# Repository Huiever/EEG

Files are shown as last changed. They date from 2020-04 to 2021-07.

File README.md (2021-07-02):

# 脑电放大器说明文档

version：V1.0.0         author：lyh

## 准备

- windows系统电脑一台

- 下载并安装[CH340驱动](http://www.wch.cn/downloads/file/65.html?time=2020-10-26%2015:34:02&code=aVN9CyCuR4TqbKSTNDEmppEj6408df6NMeNtbwHk)

- 下载[Openbci_GUI V4.2.0](https://github.com/OpenBCI/OpenBCI_GUI/releases/tag/v4.2.0)，更高版本目前还无法支持

- 放大器硬件接口说明

  1. **SWD程序下载接口**：烧录固件使用
  2. **电源接口**：电源输出，测试使用.`AVDD`,`AVSS`分别为`ads1299`正负输入电源，为`+-2.5V`
  3. **电极接口**：`INxP`,`INxN`(x=1,2,...,8)分别为8个通道的正负输入，`REF`为参考电极输入，`BIAS`为右腿驱动输入
  4. **电源开关**：按下为OFF，**弹起**为**ON**
  5. **`HC05`蓝牙接口**：若使用`HC05`蓝牙，将7中跳线帽选择`HC05`，同时蓝牙模块插入时应注意方向，模块朝板内，也可根据模块上的丝印匹配来插入
  6. **电池接口(背面)**：3.7V锂电池输入，**请勿反接或短路**
  7. **蓝牙选择**：利用跳线帽选择蓝牙为`nRF52832`or`HC05`
  8. **通信线路跳线帽**：连接`ads1299`和`stm32f407`,取下跳线帽则对应通信断开
  9. **充电指示灯**：充电时亮红灯，充满亮绿灯
  10. **LED显示**：放大器上丝印有误，从上往下分别为`PWR`,`LED1`,`LED0`，**电源ON**时`PWR`点亮
  11. **`MicroUSB`接口**：供电以及对电池充电，还可作为有线串口使用
  12. **按键**：`RESET`控制程序复位，`KEY1`,`KEY2`为自定义按键，编程使用

  

## 开始

1. 打开`Openbci_GUI`，将microUSB线一端插入电脑，另一端接入放大器

2. 对脑电电极涂上导电膏，固定在头部，另一端根据需要接在放大器的指定位置.采用单极导联的时候，参考电极接`REF`，其余电极接`INxP`.双极导联的时候`INxP`,`INxN`交替连接.程序默认为单极导联模式

3. 打开放大器的电源开关

4. 在`Openbci_GUI`界面，依次点选`LIVE(from Cyton)`,`Serial(from Dongle)`，最后点击`AUTO_CONNECT`等待数秒钟即可启动放大器并进入波形显示界面

   
   


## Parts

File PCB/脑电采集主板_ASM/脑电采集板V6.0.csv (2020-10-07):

Comment | Description | Designator | Footprint | LibRef | Pins | Quantity
100nF | 贴片电容 | C1, C3, C6, C7, C8, C11, C12, C28, C46, C47, C48, C49, C50, C51, C52, C53, C54, C55, C56, C57, C89, C93 | 0402_C | 0402 100nF (104) 10% 16V | 2 | 22
10uF | 贴片电容 | C2, C9, C10, C13, C15, C17, C18, C20, C23, C24, C32, C33, C88 | 0402_C | 0402 10uF (106) 20% 6.3V | 2 | 13
10uF (106) 20% 6.3V | 贴片电容 | C4 | 0402_C | 0402 10uF (106) 20% 6.3V | 2 | 1
100nF (104) 10% 16V | 贴片电容 | C5 | 0402_C | 0402 100nF (104) 10% 16V | 2 | 1
1uF | 贴片电容 | C14, C16, C19, C21, C25, C26, C27 | 0402_C | 0603 1uF (105) 10% 50V | 2 | 7
2.2uF | 贴片电容 | C22, C30, C31 | 0603_C | 0603 2.2uF (225) 10% 16V | 2 | 3
10nF | 贴片电容 | C29, C34, C75 | 0402_C | 0402 10nF (103) 10% 50V | 2 | 3
10pF | 贴片电容 | C35, C36 | 0402_C | 0603 10pF (100) 5% 50V | 2 | 2
22pF | 贴片电容 | C37, C38, C90, C96 | 0402_C | 0603 22pF (220) 5% 50V, 0402 22pF (220) 5% 50V | 2 | 4
10uF 10V | 贴片电容 | C39, C43 | 0402_C | 0603 10uF (106) 10% 10V | 2 | 2
100nF 50V | 贴片电容 | C40, C41, C44 | 0402_C | 0603 100nF (104) 10% 50V | 2 | 3
2.2uF 16V | 贴片电容 | C42 | 0603_C | 0603 2.2uF (225) 10% 16V | 2 | 1
2.2uF (225) 10% 16V | 贴片电容 | C45 | 0603_C | 0603 2.2uF (225) 10% 16V | 2 | 1
4.7nF | 贴片电容 | C58, C59, C60, C61, C62, C63, C64, C65, C66, C67, C68, C69, C70, C71, C72, C73, C74 | 0603_C | 0402 4.7nF (472) 10% 50V | 2 | 17
1uF 50V | 贴片电容 | C76, C78, C80, C82, C84, C86 | 0402_C | 0603 10nF (103) 10% 50V | 2 | 6
100nF 50V | 贴片电容 | C77, C79, C81, C83, C85, C87 | 0402_C | 0603 10nF (103) 10% 50V | 2 | 6
100uF | 钽电容 | C91 | CASE-B_3528 | 3528 100uF (107) 10% 6.3V | 2 | 1
1uF | 贴片电容 | C92, C94, C95 | 0603_C | 0603 1uF (105) 10% 50V | 2 | 3
SS210 | 二极管 | D1 | SMA(DO-214AC)_S1 | SMA(DO-214AC) SS210 | 2 | 1
红灯 0603 | 发光二极管 | D2, LED0 | 0603_LED_S1 | 0603 红灯 | 2 | 2
绿灯 0603 | 发光二极管 | D3, LED1, PWR | 0603_LED_S1 | 0603 绿灯 | 2 | 3
Fuse 1A | Fuse | F1 | 0805_R | Fuse 2 | 2 | 1
SW-PB | Switch | KEY1, KEY2, RESET | KEY_3.6*2.5 | SW-PB | 2 | 3
3.3uH±10% | 贴片电感 | L1, L2, L3, L4 | 0805_L | 0805 3.3uH10% | 2 | 4
蓝牙选择 | Header, 3-Pin, Dual row | P1 | HDR2X3 | Header 3X2 | 6 | 1
HC-05_CON | Header, 6-Pin | P2 | HDR1X6 | Header 6 | 6 | 1
USB | Header, 5-Pin | P3 | MICRO-USB | Header 5 | 7 | 1
电源 | Header, 5-Pin, Dual row | P5 | HDR2X5 | Header 5X2 | 10 | 1
battery | Header, 2-Pin | P6 | HDR1X2 | Header 2 | 2 | 1
SWD | Header, 4-Pin | P7 | HDR1X4 | Header 4 | 4 | 1
Header 9X2 | Header, 9-Pin, Dual row | P8 | HDR2X9 | Header 9X2 | 18 | 1
Header 8X2 | Header, 8-Pin, Dual row | P9 | HDR2X8 | Header 8X2 | 16 | 1
BSS84LT1G | MOS(场效应管) | Q1 | SOT-23(SOT-23-3) | BSS84LT1G | 3 | 1
47KΩ | 贴片电阻 | R1, R2, R3, R5, R6 | 0402_R | 0402 47KΩ (4702) 1% | 2 | 5
4.7KΩ | 贴片电阻 | R7, R9 | 0402_R | 0402 4.7KΩ (4701) 1% | 2 | 2
120Ω | 贴片电阻 | R8, R10, R12, R13 | 0402_R | 0402 120Ω (1200) 1% | 2 | 4
10KΩ | 贴片电阻 | R11 | 0402_R | 0402 10KΩ (1002) 1% | 2 | 1
100KΩ | 贴片电阻 | R14, R15 | 0402_R | 0402 100KΩ (1003) 1% | 2 | 2
1.2KΩ | 贴片电阻 | R16 | 0402_R | 0402 1.2KΩ (1201) 1% | 2 | 1
1KΩ | 贴片电阻 | R17, R21 | 0402_R | 0402 1KΩ (1001) 1%, 0603 1KΩ (1001) 1% | 2 | 2
0Ω | 贴片电阻 | R18 | 0402_R | 0603 0Ω (0R0) 1% | 2 | 1
510Ω | 贴片电阻 | R19, R20 | 0402_R | 0603 510Ω (5100) 1% | 2 | 2
1MΩ | 贴片电阻 | R22 | 0402_R | 0603 1.2MΩ (1204) 1% | 2 | 1
10K | 贴片电阻 | R23, R26, R27, R28, R29 | 0402_R | 0603 10Ω (10R0) 1% | 2 | 5
10Ω | 贴片电阻 | R24 | 0402_R | 0603 10Ω (10R0) 1% | 2 | 1
10Ω (10R0) ±1% | 贴片电阻 | R25 | 0402_R | 0603 10Ω (10R0) 1% | 2 | 1
4.99KΩ | 贴片电阻 | R30, R31, R32, R33, R34, R35, R36, R37, R38, R39, R40, R41, R42, R43, R44, R45, R46 | 0603_R | 0603 4.99KΩ (4991) 1% | 2 | 17
390KΩ | 贴片电阻 | R47 | 0603_R | 0603 390KΩ (3903) 1% | 2 | 1
2KΩ | 贴片电阻 | R48 | 0402_R | 0402 2KΩ (2001) 1% | 2 | 1
0Ω (0R0) ±1% | 贴片电阻 | R49 | 0402_R | 0402 0Ω (0R0) 1% | 2 | 1
SW-PB | Switch | S1 | KEY_5.8*5.8 | SW-PB | 6 | 1
nRF52832 |  | U1 | nRF52832 | nRF52832 | 24 | 1
TF_Card |  | U2 | TF_1 | TF_Card | 14 | 1
CH340G | USB | U3 | SOIC-16_150mil | CH340G_[C14267] | 16 | 1
MPU-6050 | 传感器 | U4 | QFN-24_4x4x05P | MPU-6050_[C24112] | 25 | 1
TP4056 | 电池电源管理 | U5 | SOP-8_EP_150mil | TP4056_[C16581] | 9 | 1
TPS60403 |  | U6 | SOT-23-5 | TPS60403 | 5 | 1
TPS73225 |  | U7 | SOT-23-5 | TPS73225 | 5 | 1
TPS71733DCKR |  | U8 | SC-70-5 | TPS71733DCKR | 5 | 1
TPS72325 |  | U9 | SOT-23-5 | TPS72325 | 5 | 1
STM32F429ZGT6 | ARM | U10 | LQFP-144_20x20x05P | STM32F429ZGT6 | 144 | 1
ADS1299IPAG |  | U11 | ADS1299 | ADS1299IPAG | 64 | 1
32.768KHz | 贴片晶振 | Y1 | SMD-3215_2P FC - 135 | SMD-3215_2P 32.768KHz 20ppm 12.5pF | 2 | 1
8MHz | 贴片晶振 | Y2 | SMD-5032_2P | SMD-5032_2P 8MHz 20ppm 20pF | 2 | 1
12MHZ | 贴片晶振 | Y3 | SMD-3225_4P | SMD-3225_4P 12MHZ 20PF 10PPM | 4 | 1

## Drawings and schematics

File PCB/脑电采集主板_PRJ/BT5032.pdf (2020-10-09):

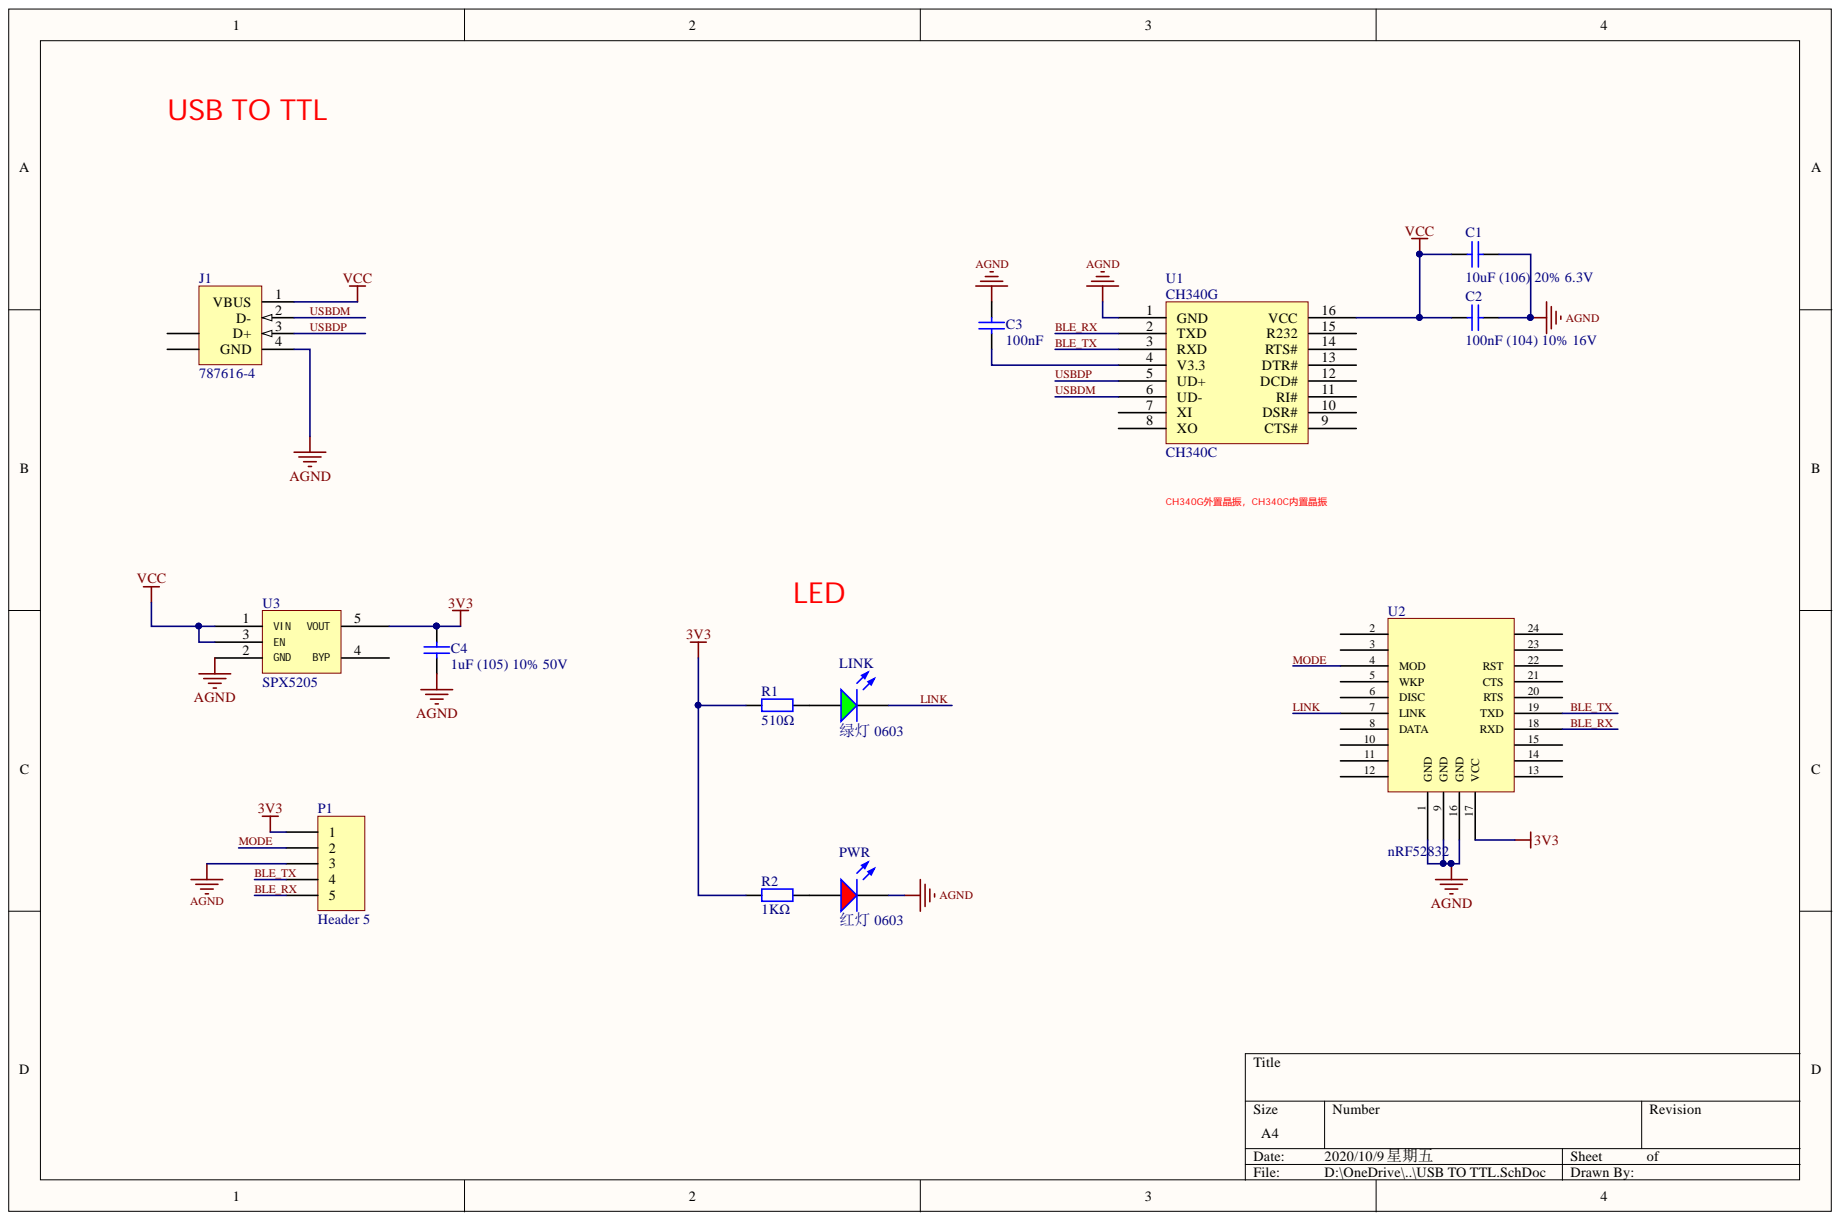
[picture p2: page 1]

VCC 17 RXD 18 TXD 19 RTS 20 CTS 21 RST 22

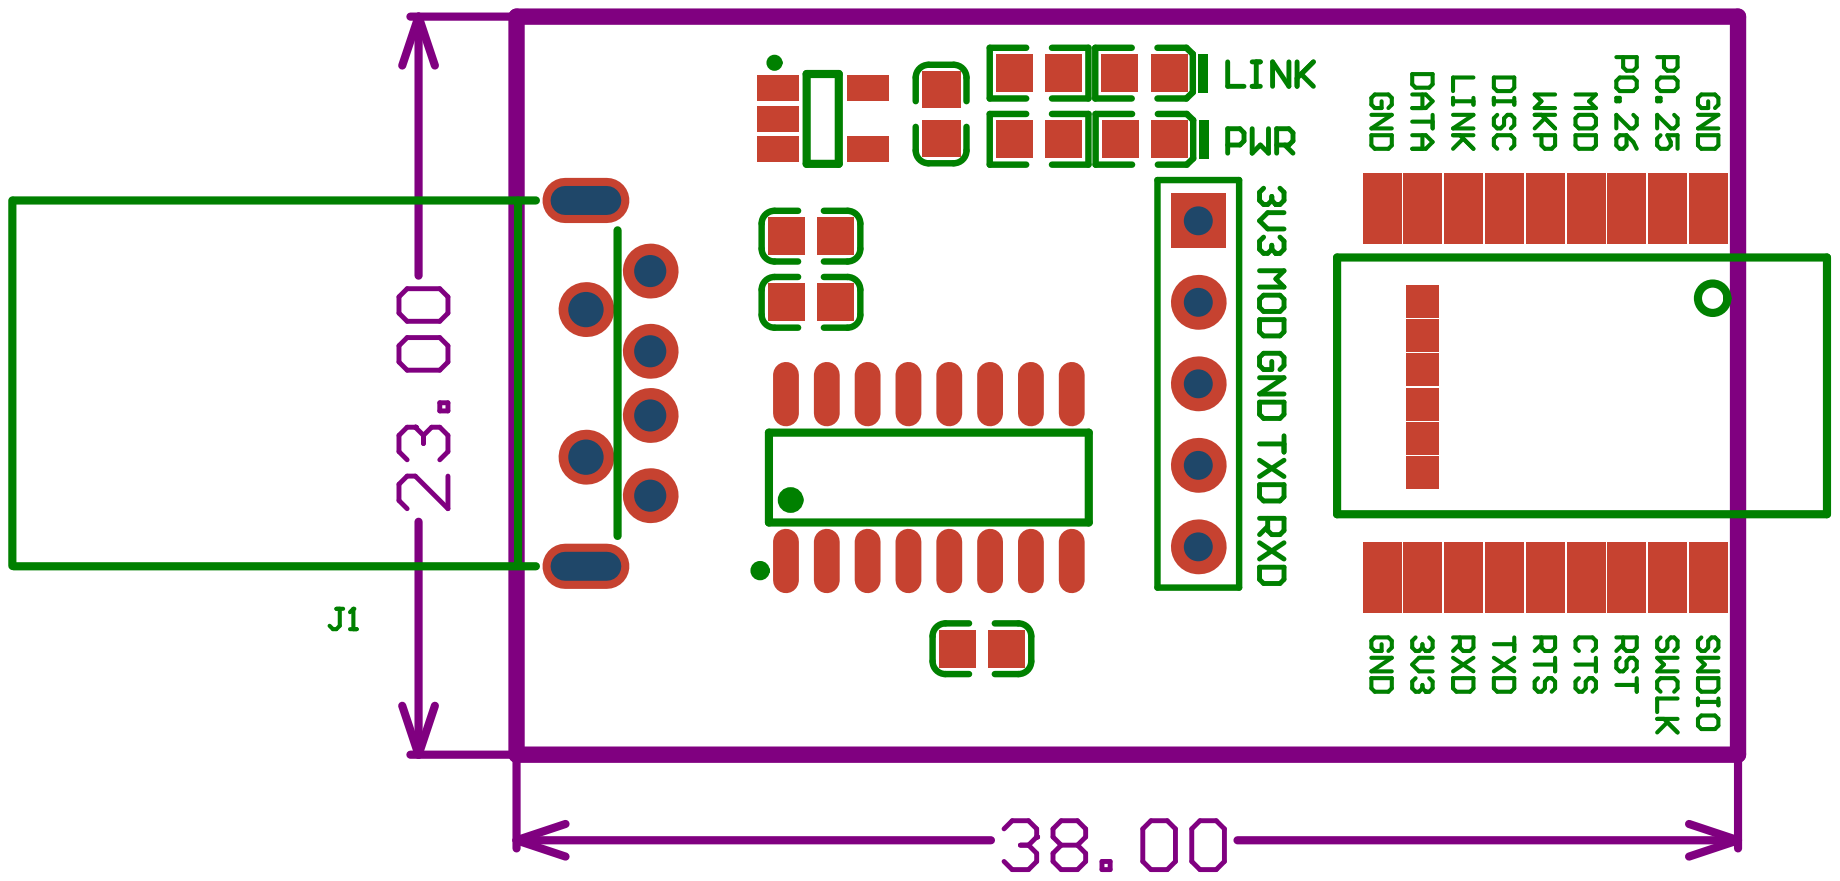
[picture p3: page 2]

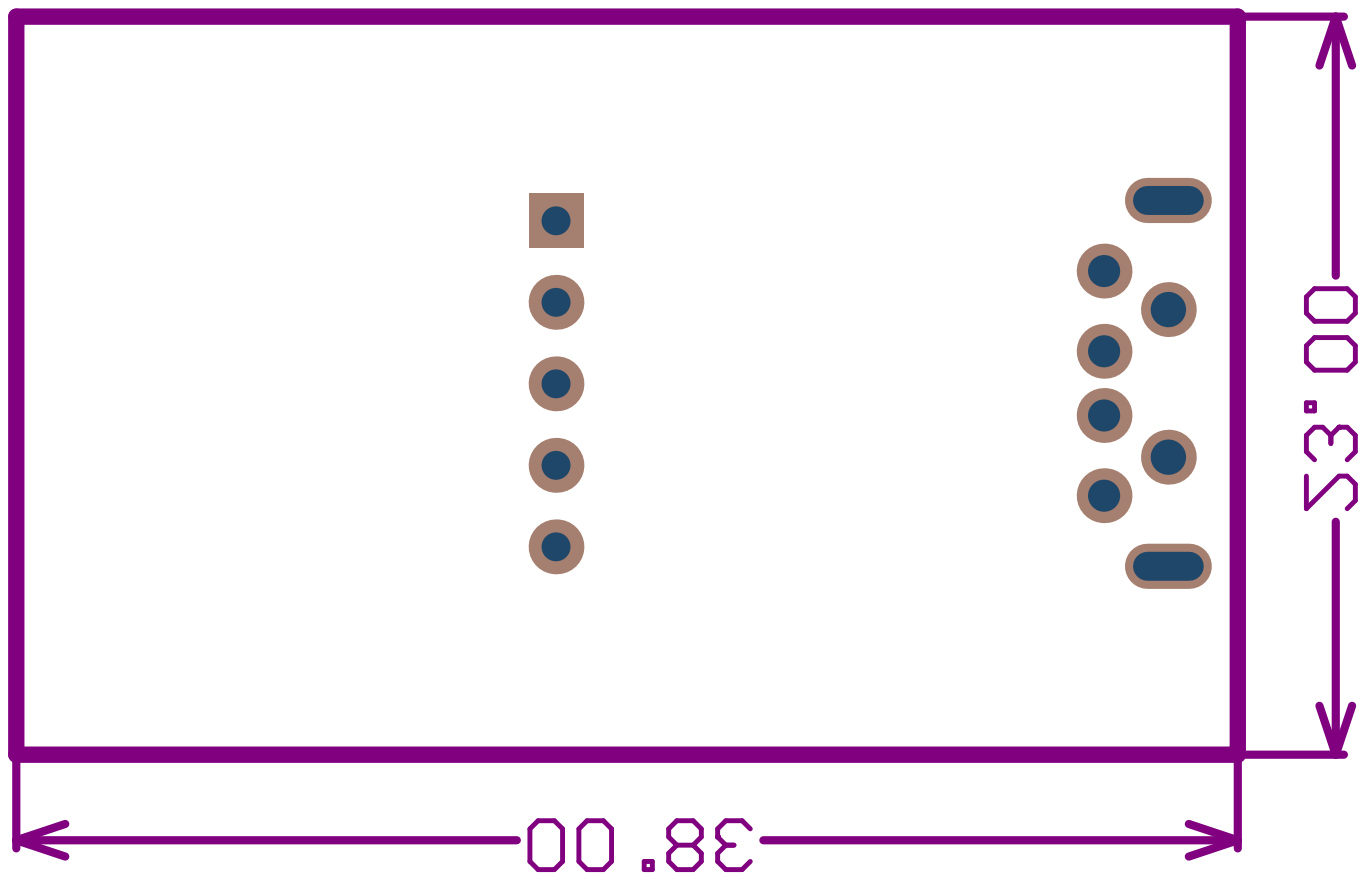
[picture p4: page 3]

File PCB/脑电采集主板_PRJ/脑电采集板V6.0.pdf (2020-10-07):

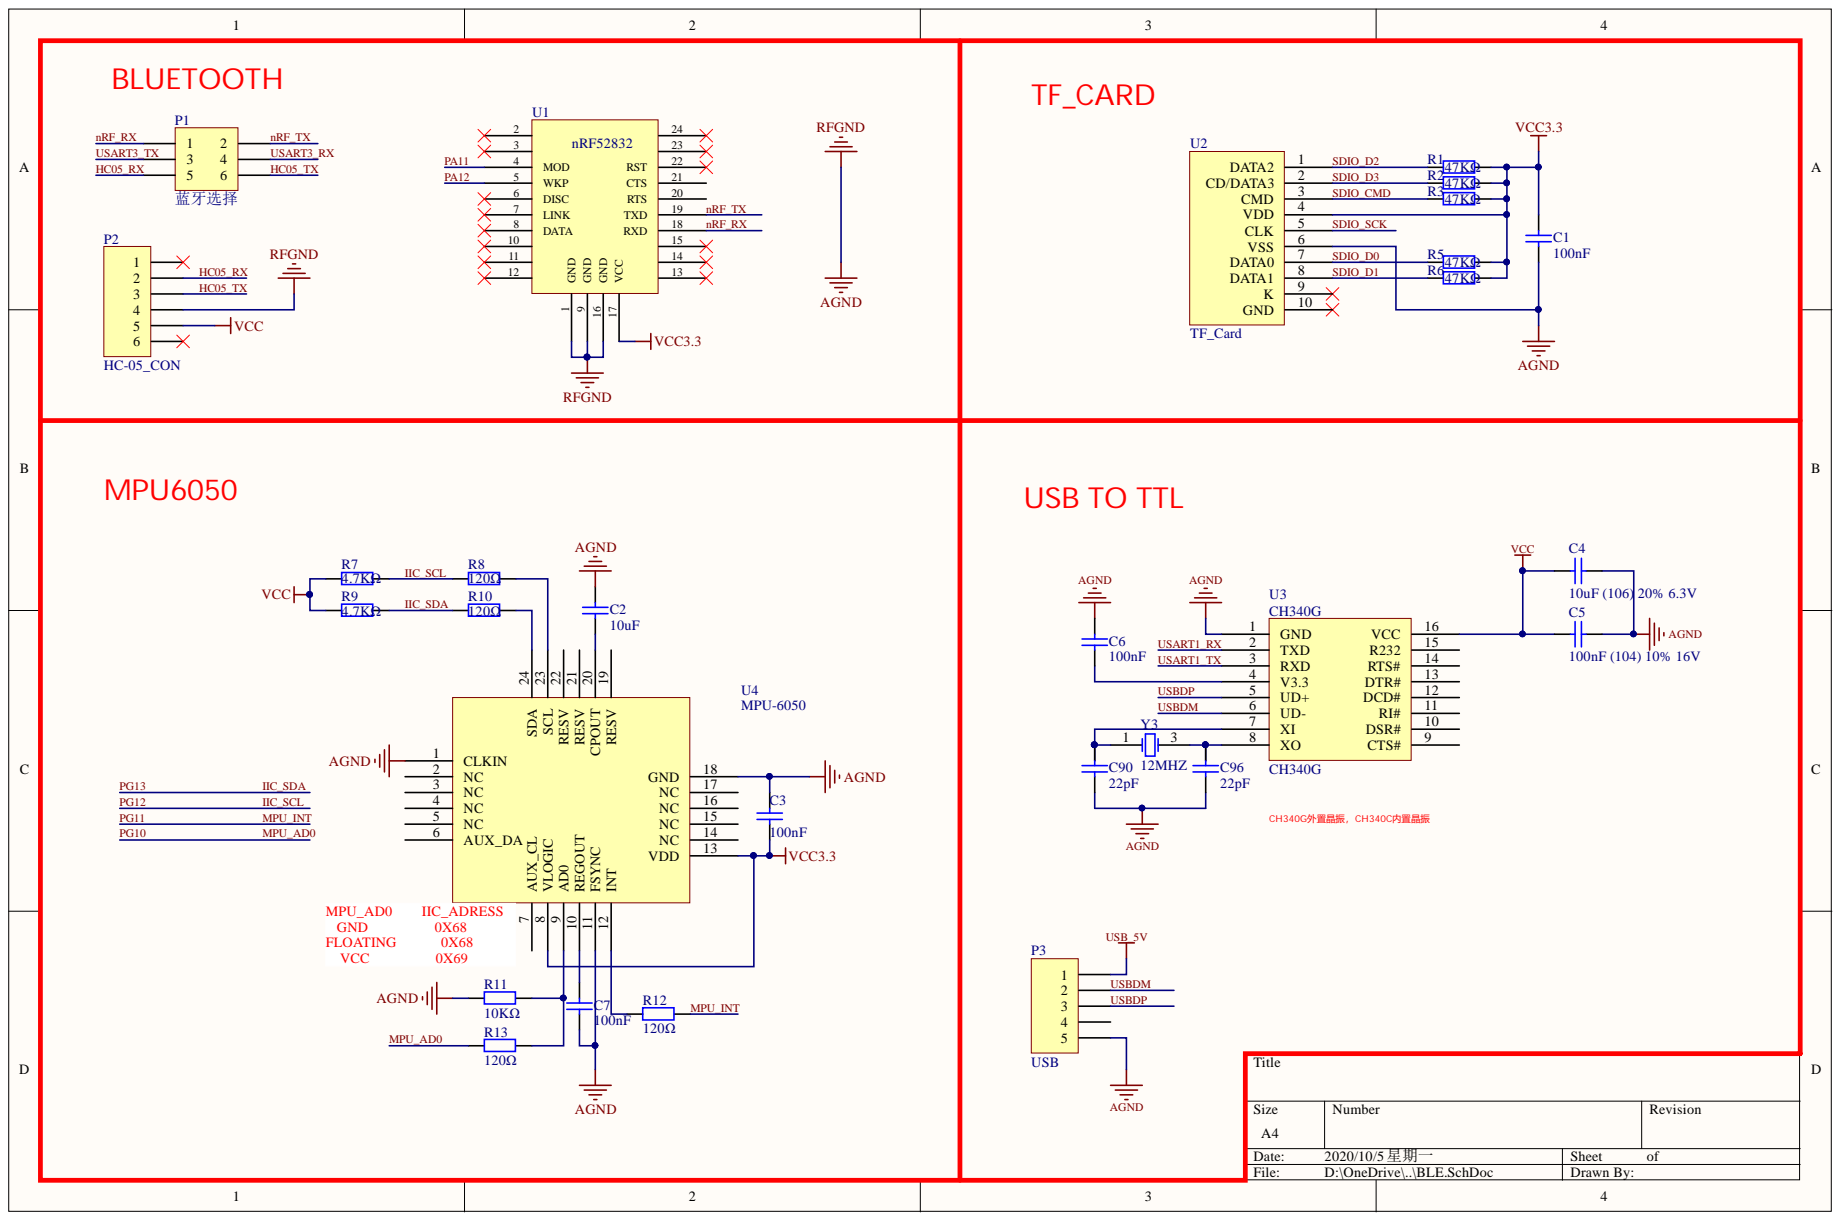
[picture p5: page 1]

VCC 17 RXD 18 TXD 19 RTS 20 CTS 21 RST 22

RESV 19 CPOUT 20 RESV 21 RESV 22 SCL 23 SDA 24

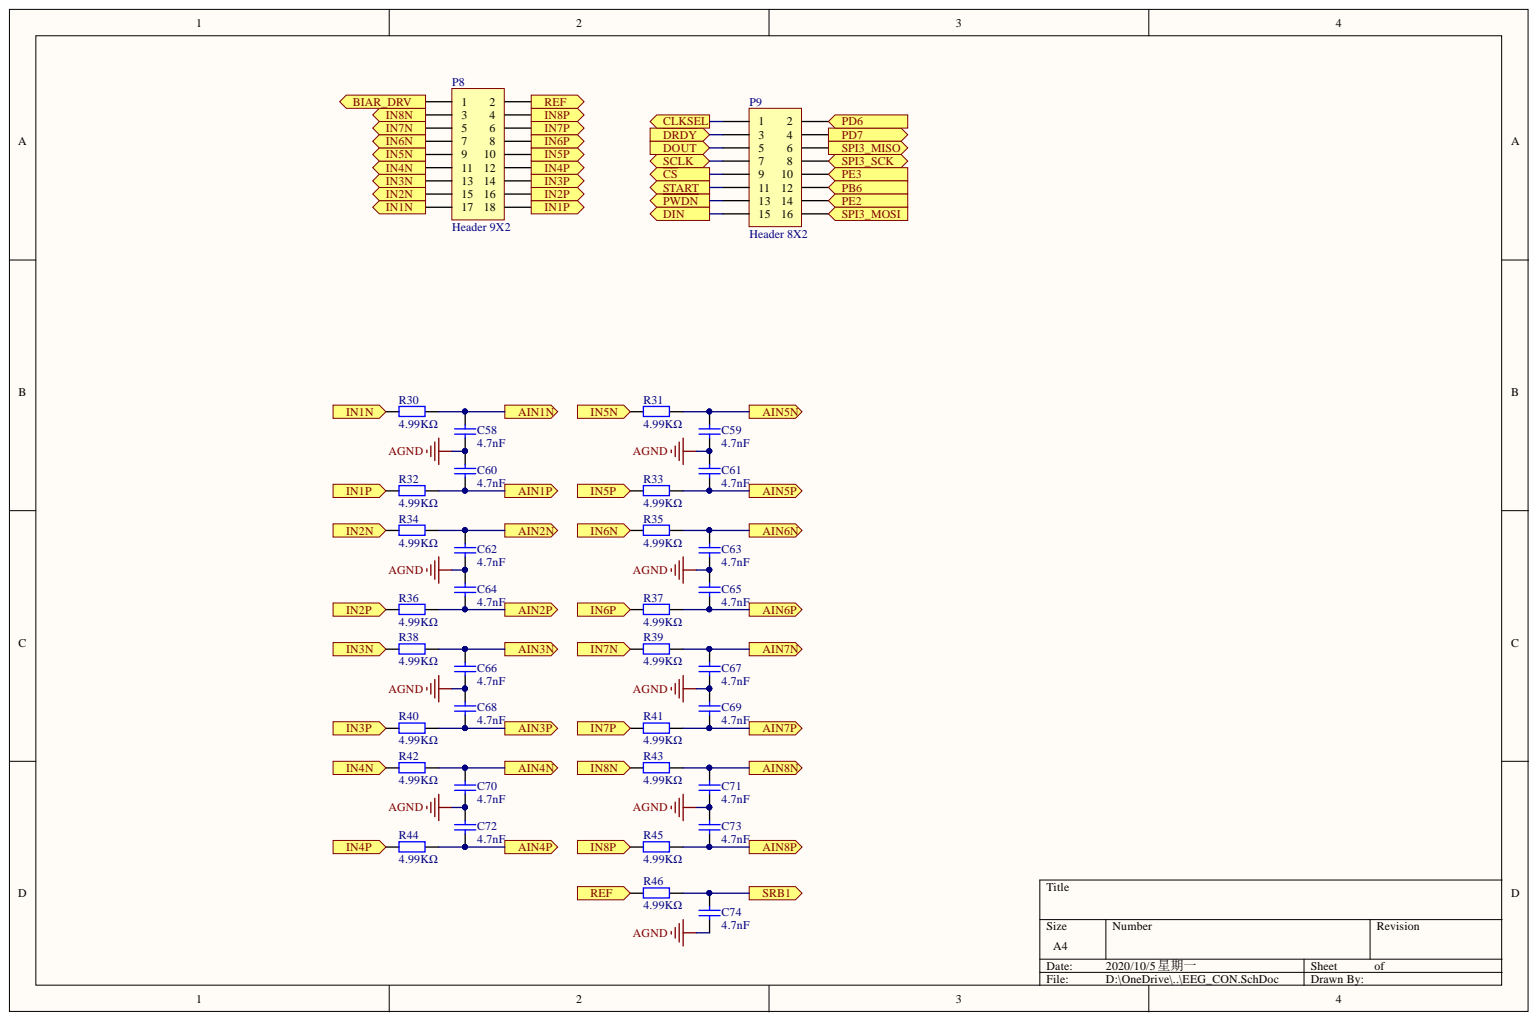
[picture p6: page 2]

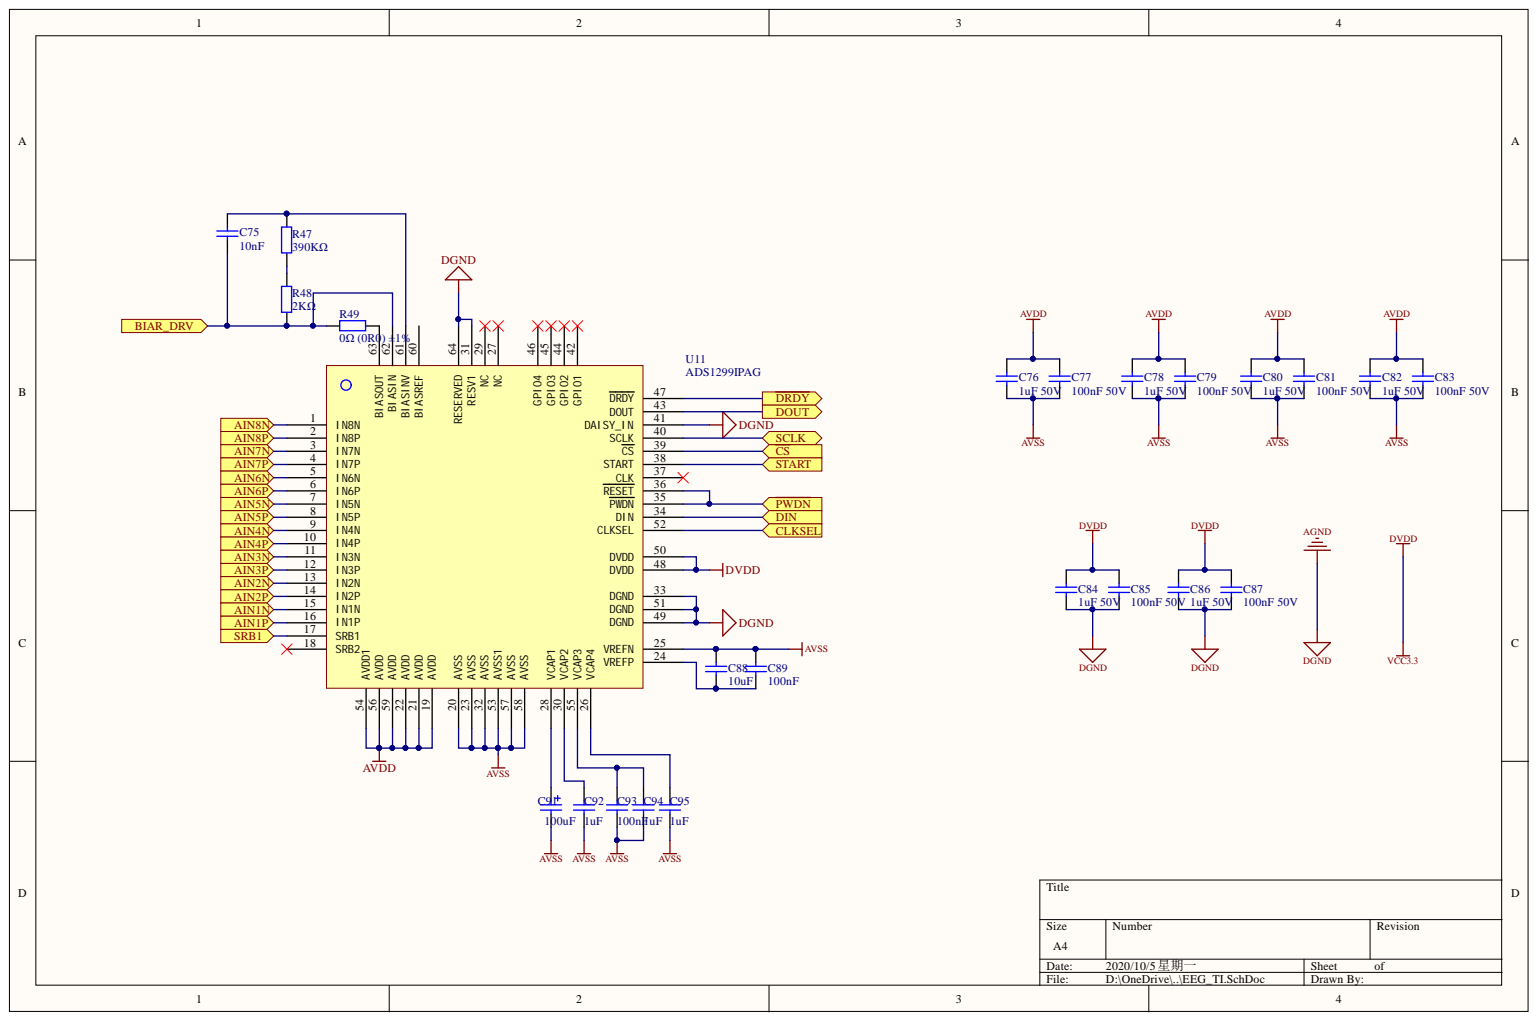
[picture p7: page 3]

BIASREF 60 BIASINV 61 BIASIN 62 BIASOUT 63

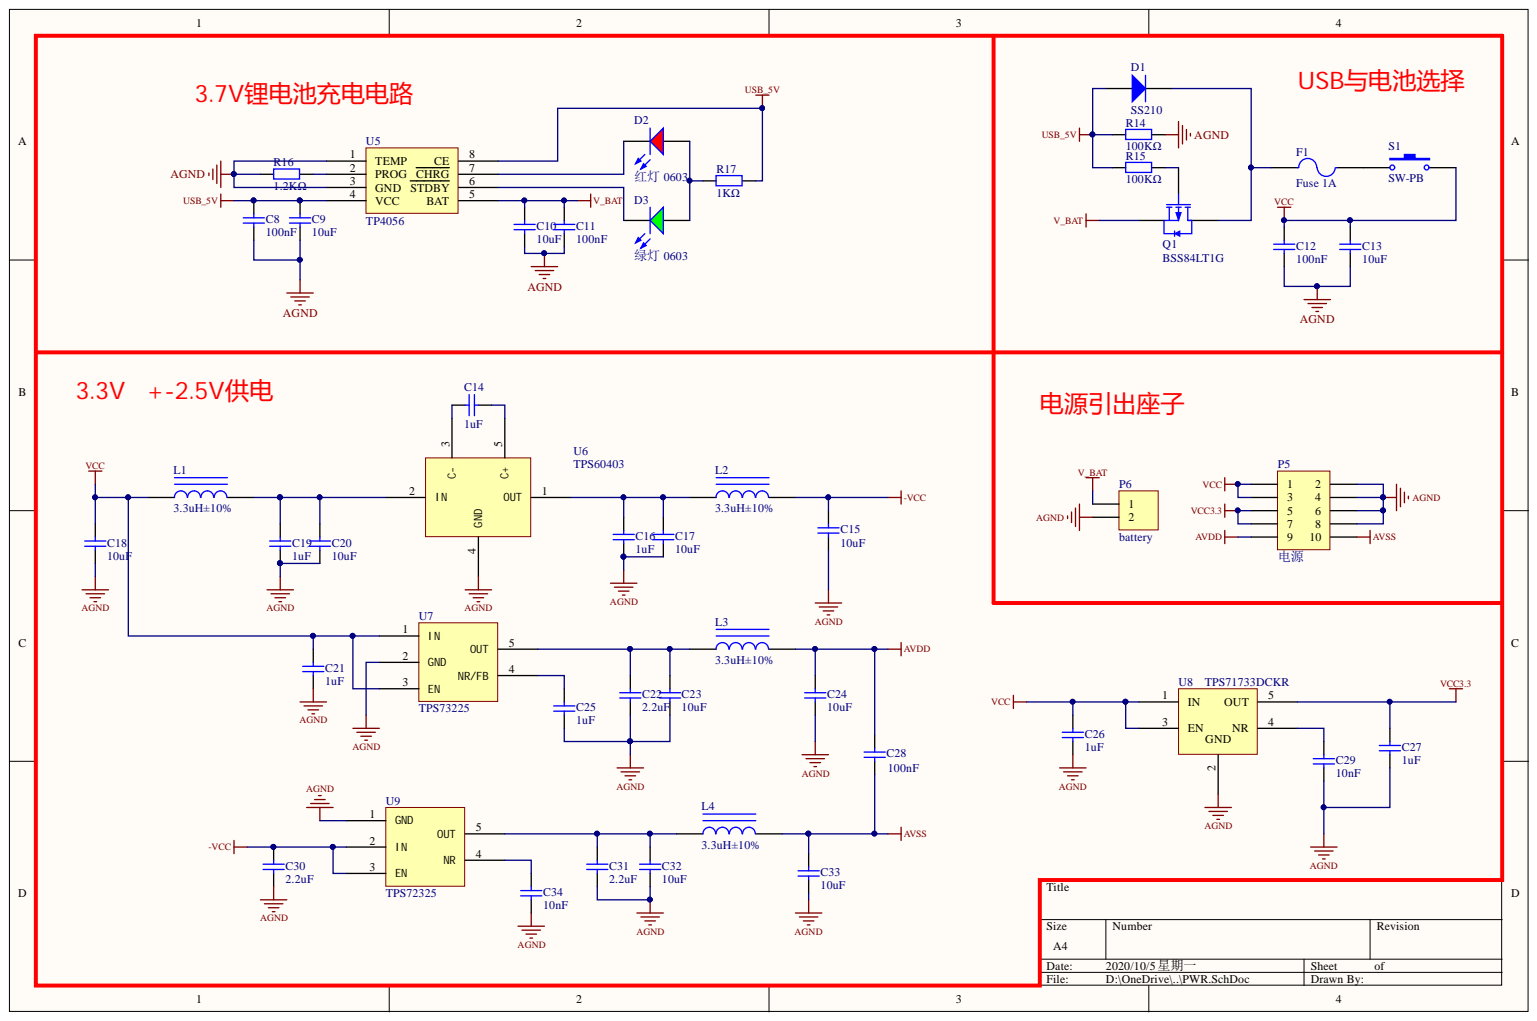
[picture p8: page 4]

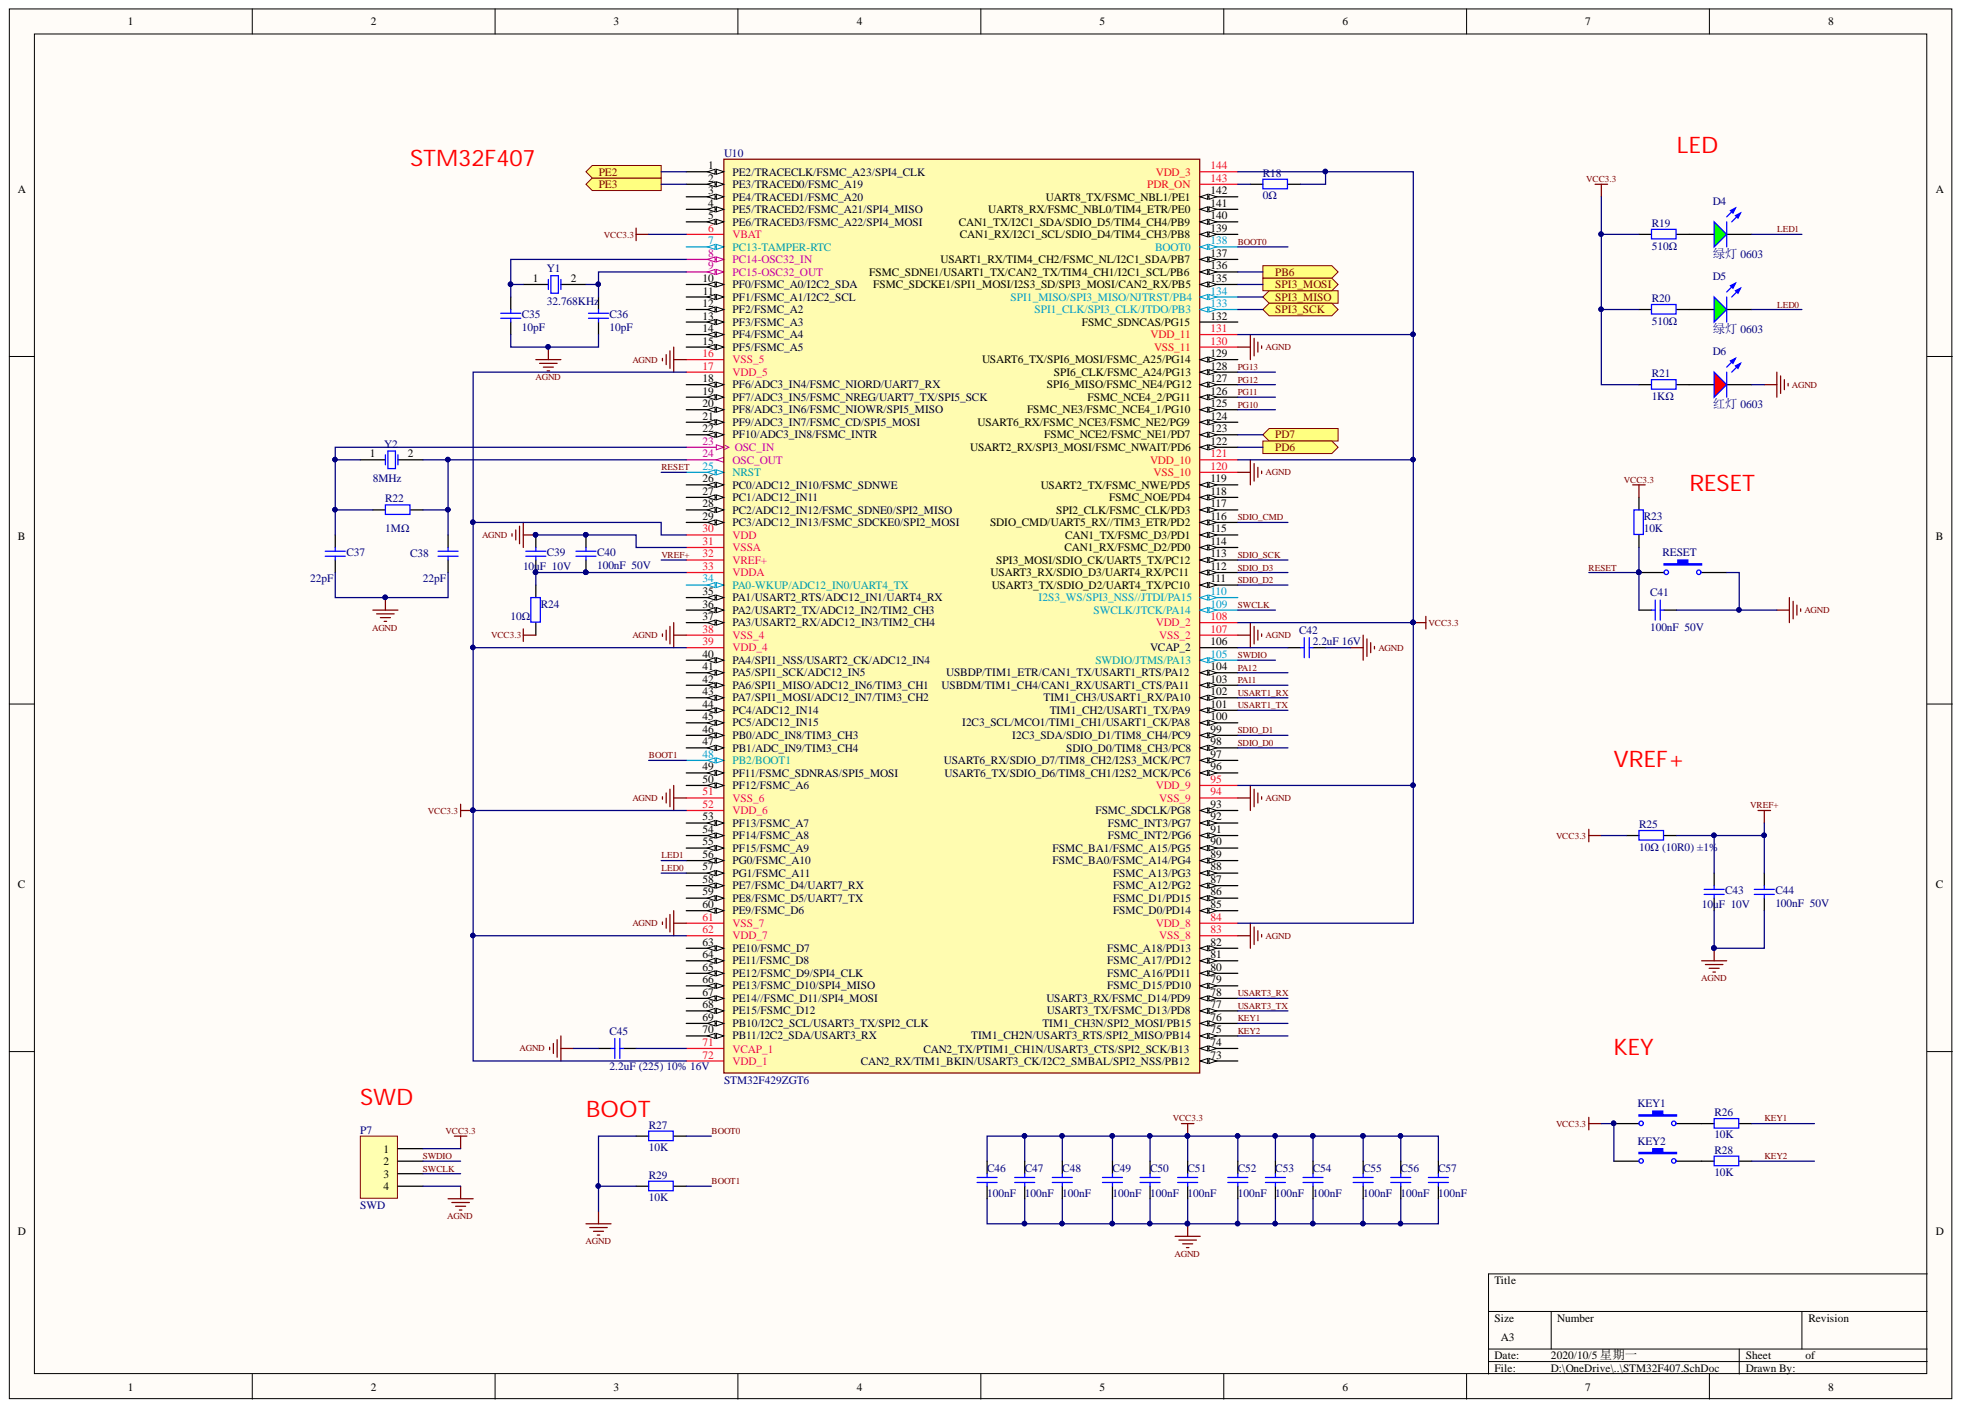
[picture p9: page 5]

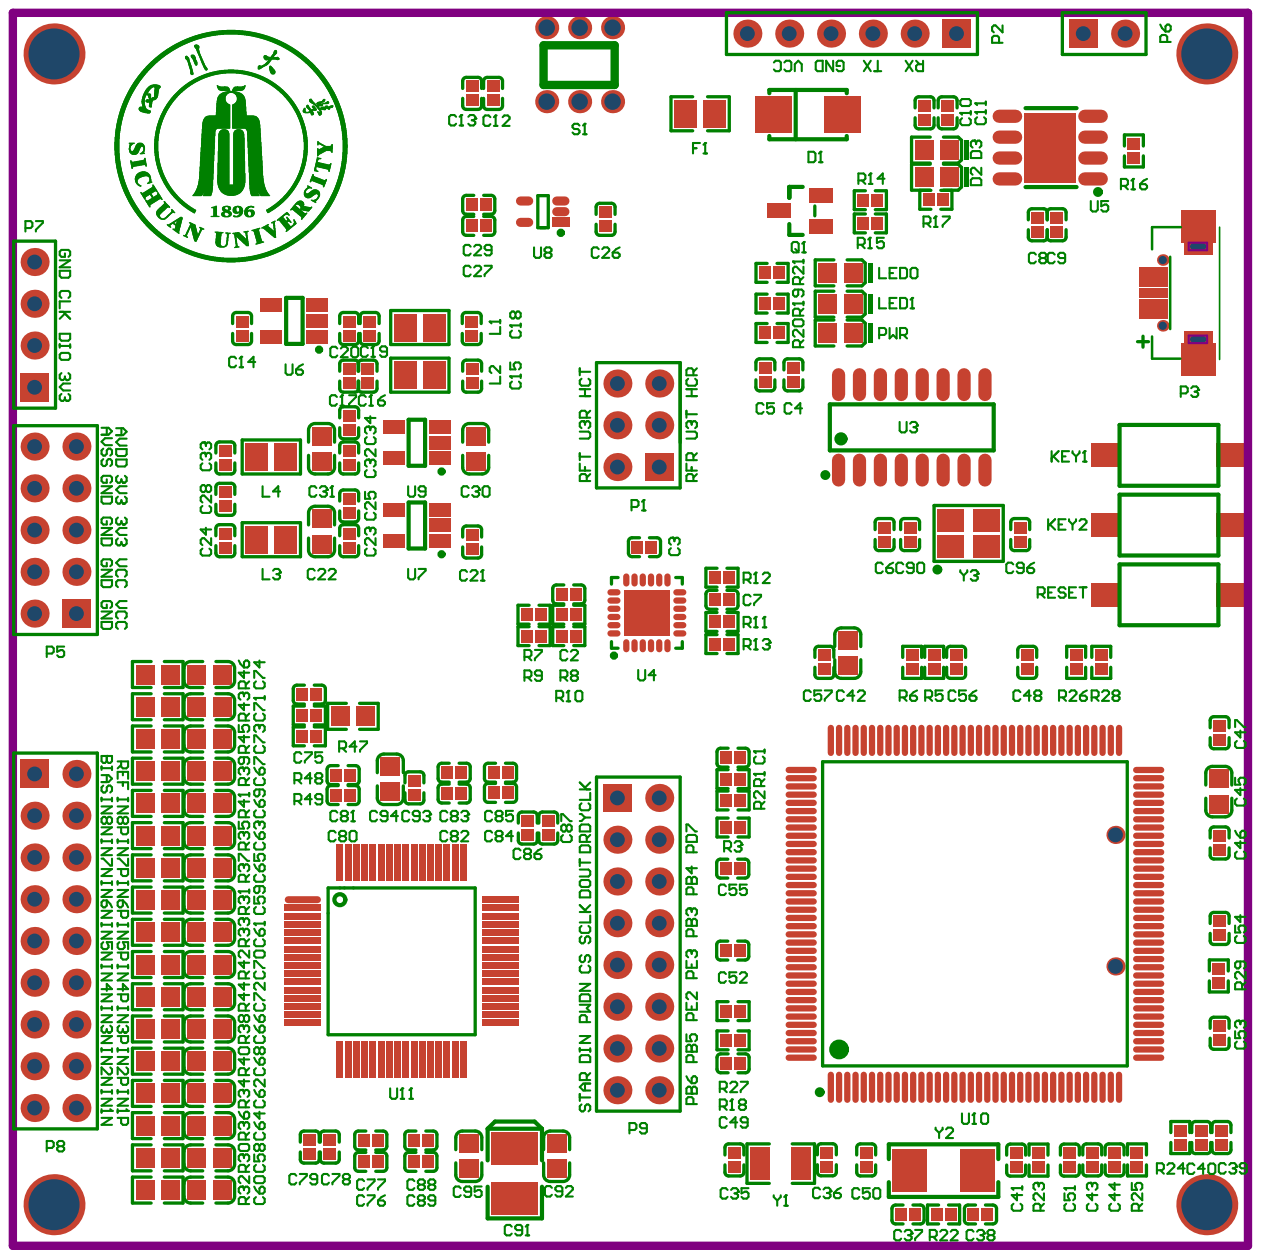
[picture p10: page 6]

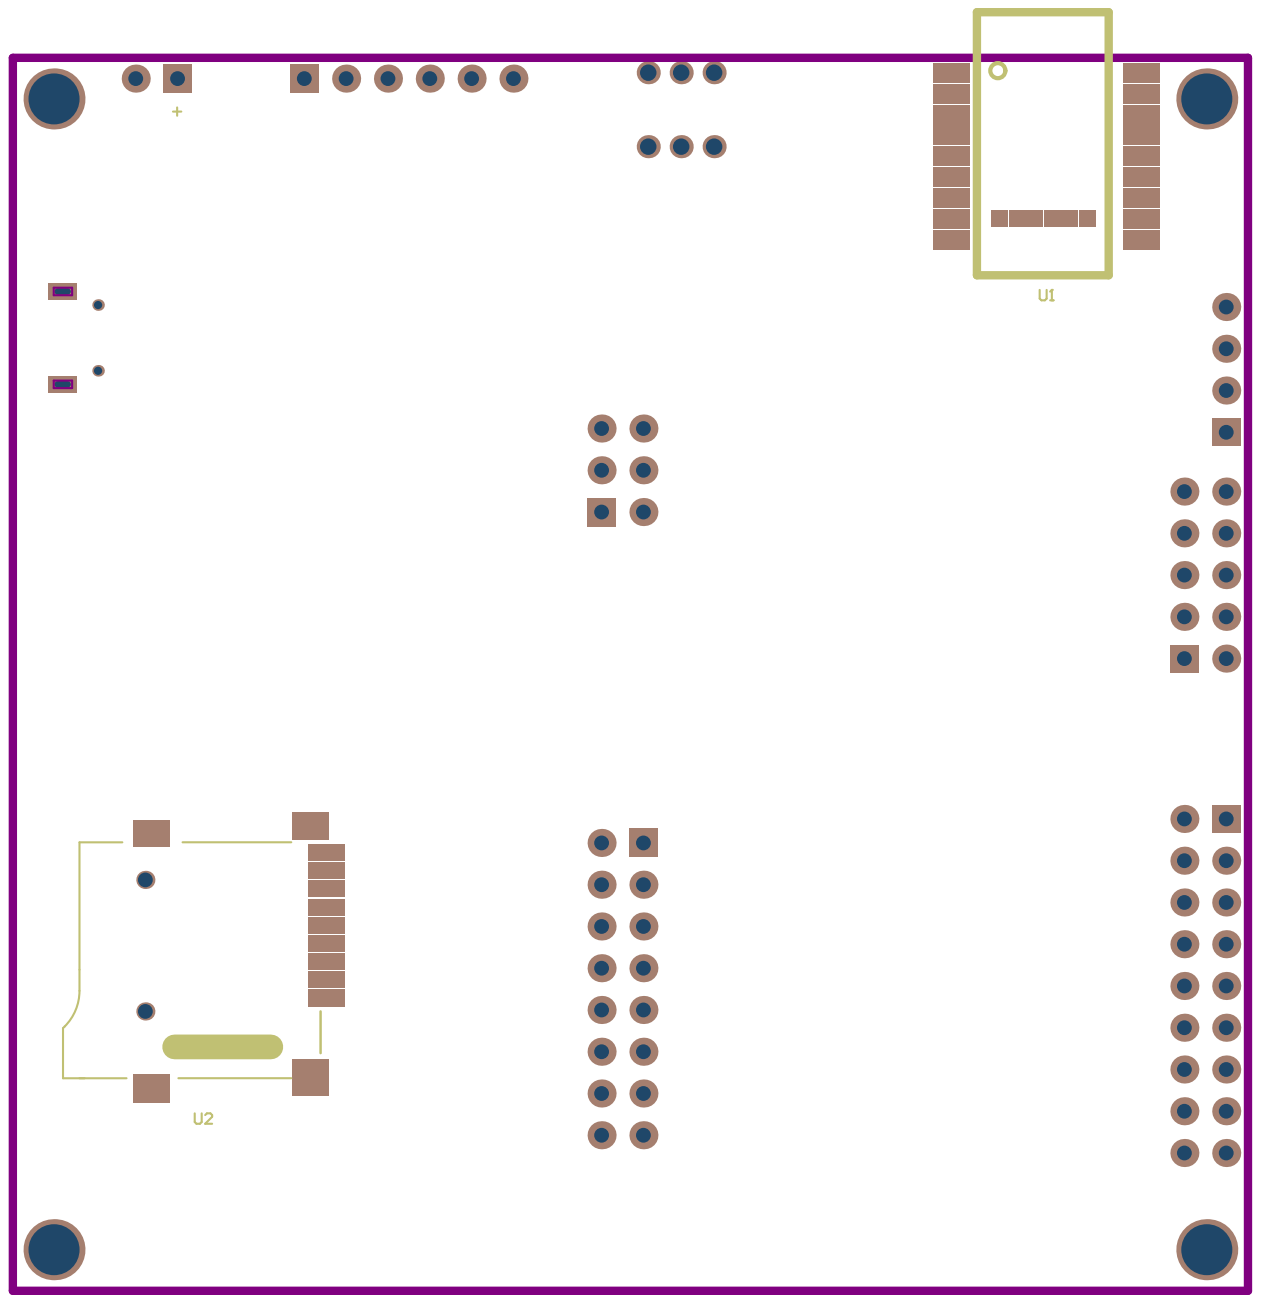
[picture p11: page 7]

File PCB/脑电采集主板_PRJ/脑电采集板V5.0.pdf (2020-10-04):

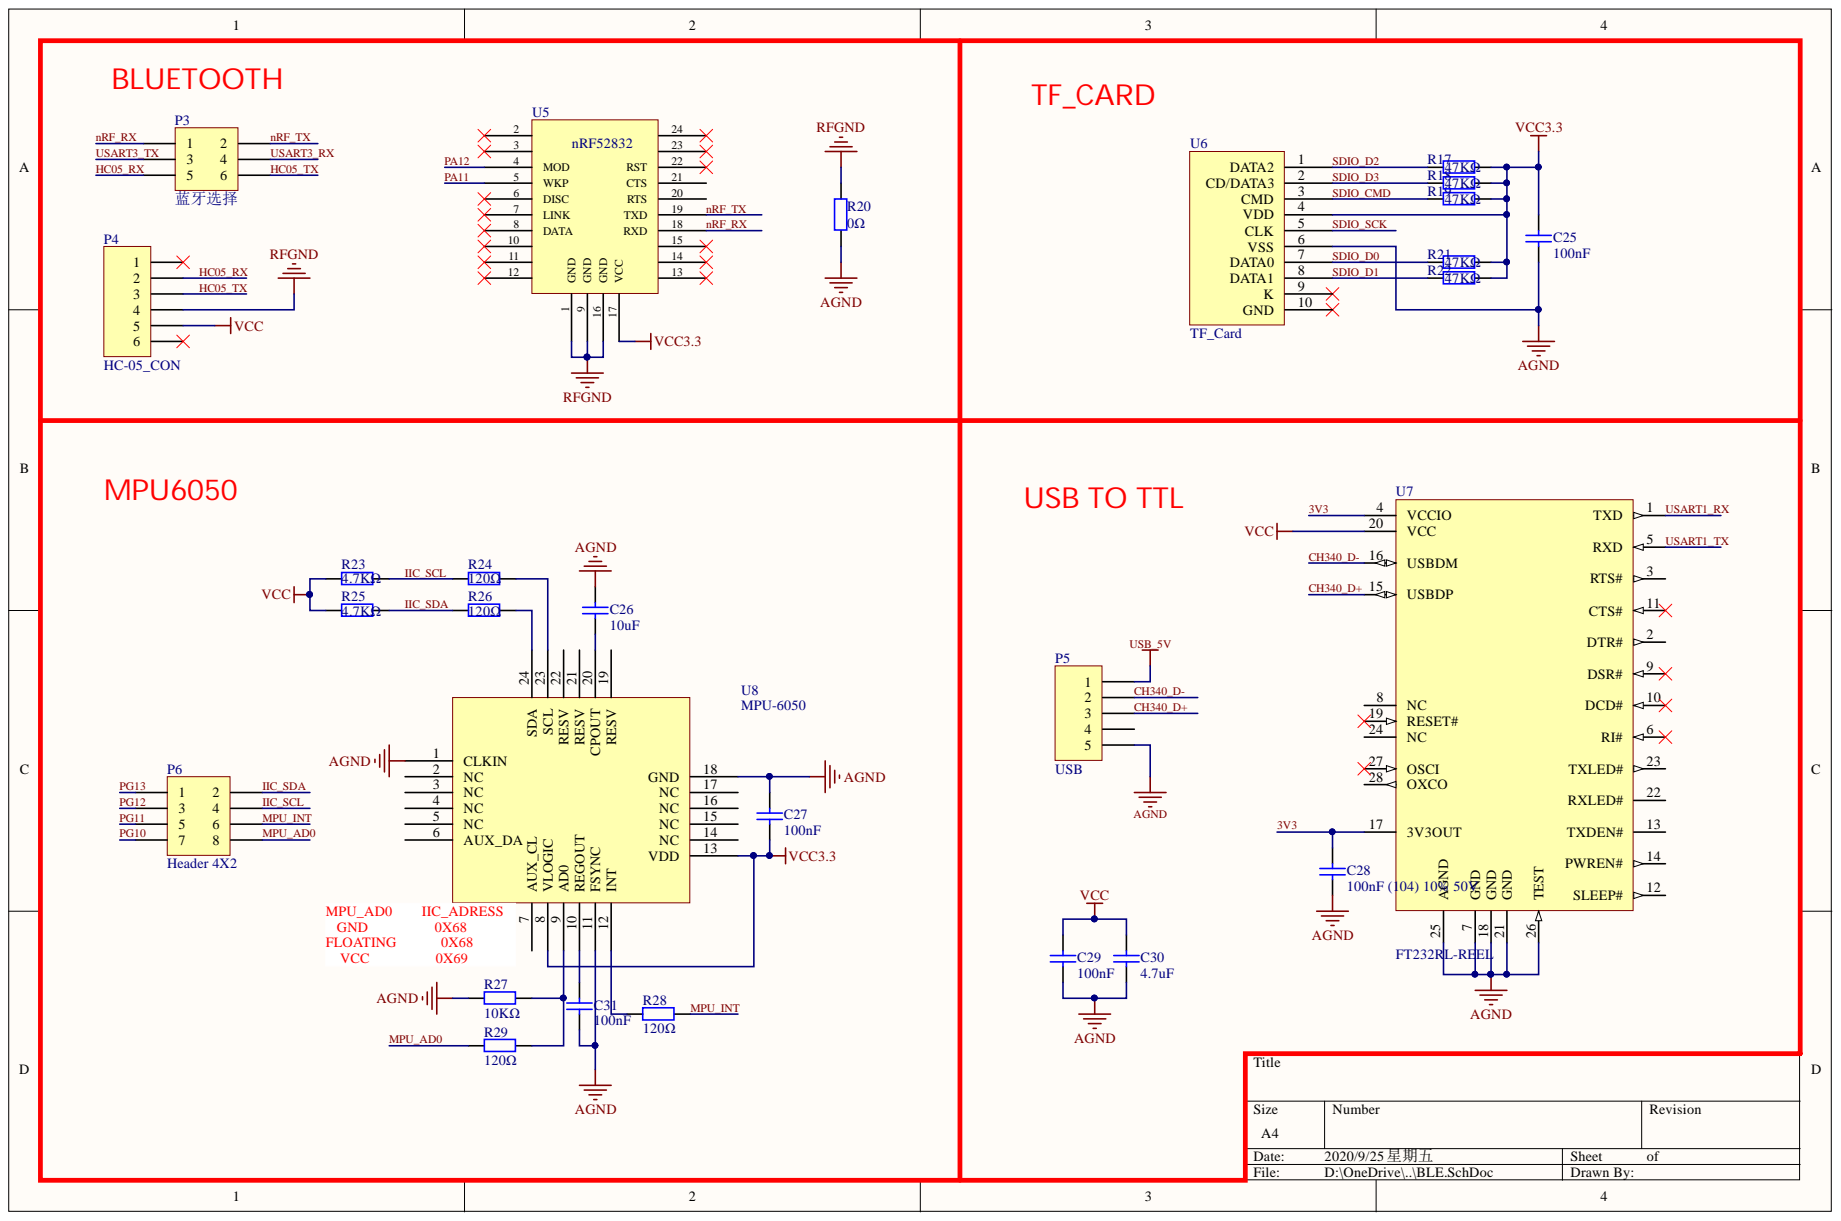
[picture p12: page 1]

RESV 19 CPOUT 20 RESV 21 RESV 22 SCL 23 SDA 24

MPU _ A D 0 IIC_ A DRESS G N D 0 X 6 8 FL O ATIN G 0 X 6 8 VCC 0 X 6 9

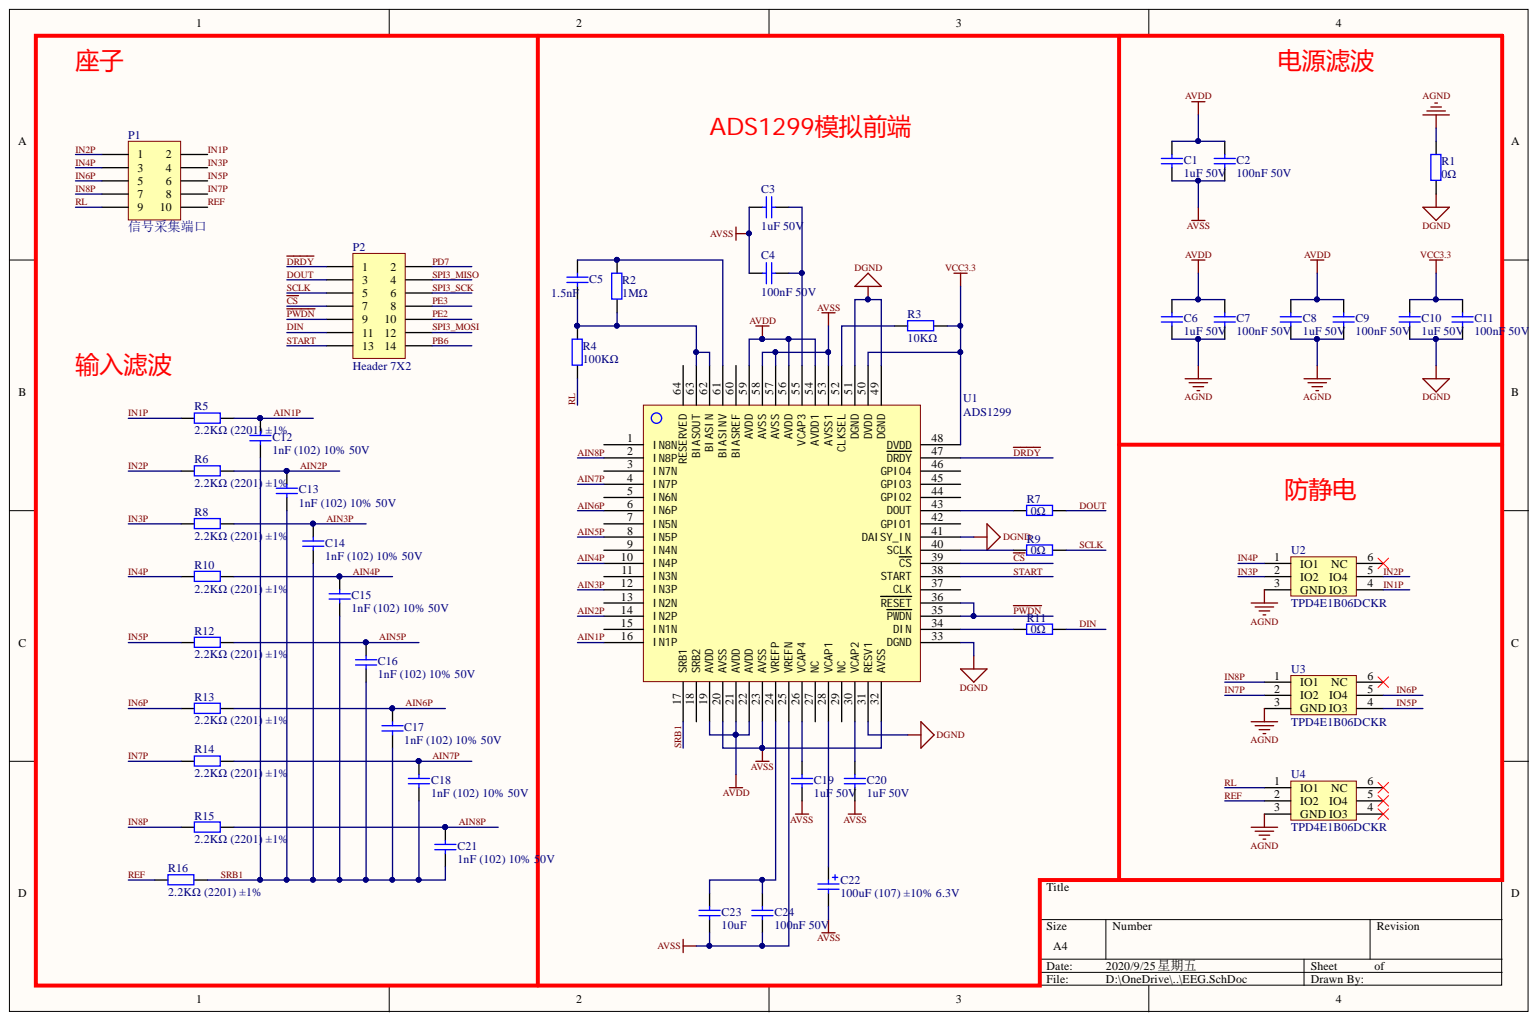
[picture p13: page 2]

GND 49 DVDD 50 DGND 51 CLKSEL 52 AVSS1 53 AVDD1 54 VCAP3 55 AVDD 56 AVSS 57 AVSS 58 AVDD 59 BIASREF 60 BIASINV 61 BIASIN 62 BIASOUT 63 RESERVED 64



1 1 | SPI3_M ISO

H z | | SPI3_SC K




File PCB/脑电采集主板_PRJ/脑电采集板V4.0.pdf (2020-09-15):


GND 49 DVDD 50 DGND 51 CLKSEL 52 AVSS1 53 AVDD1 54 VCAP3 55 AVDD 56 AVSS 57 AVSS 58 AVDD 59 BIASREF 60 BIASINV 61 BIASIN 62 BIASOUT 63 RESERVED 64



1 1 | SPI3_M ISO

H z | | SPI3_SC K




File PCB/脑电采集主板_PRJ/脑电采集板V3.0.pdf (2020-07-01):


VCC 17 RXD 18 TXD 19 RTS 20 CTS 21 RST 22


GND 49 DVDD 50 DGND 51 CLKSEL 52 AVSS1 53 AVDD1 54 VCAP3 55 AVDD 56 AVSS 57 AVSS 58 AVDD 59 BIASREF 60 BIASINV 61 BIASIN 62 BIASOUT 63 RESERVED 64



1 1 | SPI3_M ISO

H z | | SPI3_SC K




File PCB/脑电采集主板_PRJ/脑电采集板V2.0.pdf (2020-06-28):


VCC 17 RXD 18 TXD 19 RTS 20 CTS 21 RST 22


GND 49 DVDD 50 DGND 51 CLKSEL 52 AVSS1 53 AVDD1 54 VCAP3 55 AVDD 56 AVSS 57 AVSS 58 AVDD 59 BIASREF 60 BIASINV 61 BIASIN 62 BIASOUT 63 RESERVED 64






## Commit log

2020-03-25 更改元器件value
    [EEG.SchDoc]
2020-03-25 增加5转3.3V电路
    [EEG.PrjPCB, EEG.SchDoc]
2020-03-26 add .gitignore
    [EEG.SchDoc]
2020-03-27 添加了一些封装库，对原理图进行重新排布，电源改用10u与0.1u滤波，PCB简单排布
    [EEG.PcbDoc, EEG.PrjPCB, EEG.SchDoc]
2020-04-01 更改pcb布局
    [EEG.PcbDoc, EEG.SchDoc]
2020-04-01 铺铜优化
    [EEG.PcbDoc]
2020-04-02 铺铜走线优化
    [EEG.PcbDoc]
2020-04-02 第一版完成
    [EEG.PcbDoc]
2020-04-02 文件输出
    [EEG.GBL, EEG.GBO, EEG.GBS, EEG.GM1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]
2020-04-02 调整文件结构
    [EEG.GBL, EEG.GBO, EEG.GBS, EEG.GM1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]
2020-04-02 整理文件
    [EEG.PrjPCB]
2020-04-18 资料整合，ads1299数据读取调试正常
    [EEG.GBL, EEG.GBO, EEG.GBS, EEG.GM1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]
2020-05-01 change something
    [EEG.SchDoc]
2020-05-06 新版电路板
    [EEG.PrjPCB, EEG.SchDoc, Sheet1.SchDoc, Sheet2.SchDoc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]
2020-05-07 第二版pcb done！
    [EEG.GBL, EEG.GBO, EEG.GBS, EEG.GM1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]
2020-05-07 修改pcb中的一些规则和过孔大小
    [EEG.PrjPCB, Pick Place for 脑电采集.csv, 脑电采集.GBL, 脑电采集.GTL]
2020-05-21 pcb布局有问题，32的vss未接地，DVDD与地短路，AVSS与AVDD短路
    [EEG.PrjPCB, Sheet1.SchDoc]
2020-06-02 第三版pcb，增加了cc2640和nRF52382两款模块的接口，mcu选用更便宜的stm32f103rct6
    [EEG.PrjPCB, EEG.SchDoc, EEG_new.GBL, EEG_new.GBO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]
2020-06-28 daily update
    [EEG.PrjPCB, EEG_new.csv, pwr.SchDoc]
2020-07-01 新版pcb采用srb1单极导联，mcu为f407，添加cc2640和nRF两款BLE5.0芯片，增加PIN1.5插针孔位，可配合市面上常见的氯化银导联线使用
    [EEG.PrjPCB, EEG.SchDoc, EEG_F4.PcbDoc, EEG_new.GBL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]
2020-07-09 数据读取有问题
    [EEG.PrjPCB, pwr.SchDoc]
2020-07-20 添加labview上位机程序，完成部分图形显示功能
2020-08-08 修改stm32代码适配openbci上位机，同步修改matlab串口读取代码
2020-08-19 新版PCB，加入充电电路
    [EEG.PrjPCB, EEG.SchDoc, EEG_V3.0.GBL, EEG_V3.0.GBO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]
2020-09-15 第五版脑电采集板完成，新加mpu6050模块，TF卡模块。
    [EEG.PrjPCB, EEG.SchDoc, EEG_F4.PcbDoc, EEG_V3.0.GBL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]
2020-10-04 第6版PCB
    [EEG.SchDoc, EEG_CON.SchDoc, EEG_TI.SchDoc, PWR2.SchDoc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]
2020-10-07 修改代码，目前板子初始上电可以正常运行，但是reset后不可以，给芯片上电一段时间后再执行代码也无法正常运行
    [PWR2.SchDoc, Pick Place for 脑电采集板V6.0.csv, STM32F407.SchDoc, ble.SchDoc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]
2020-10-09 新增无线串口模块，采用ch340c与bt5032设计；修改代码，通信正常
    [USB TO TTL.SchDoc, USB TO TTL_BT5032.PcbDoc, 脑电采集板.PrjPCB]
